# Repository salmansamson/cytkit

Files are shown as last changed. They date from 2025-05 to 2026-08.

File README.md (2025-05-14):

# Cytkit
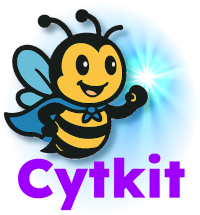
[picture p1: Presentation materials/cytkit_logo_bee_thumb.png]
Cytkit bee mascot


__Your open-source spectral cytometry sidekick__ 

## Introduction
This project was started by Samson Rogers to bring a low-cost open-source cytometer design to the cytometry community. Thanks also to Oliver Burton for contributing to the specification and Stuart Vant for starting the electronics development. The inspiration came from the Open Cytometry Hardware workshop by David Novo at CYTO 2024 in Edinburgh, and also from the OpenFlexure Microscope project by Richard Bowman and others. Thanks to many friends and colleagues for friendly advice!

Aim: to build a highly useful and accessible cytometry analyser:
- Useful for technology developers 
- Useful for laboratory hackers
- Useful for resource-limited labs
- Useful for teaching flow cytometry
- Useful for all cell biologists

Through this project, I hope to: 
- Help build the open source cytometry hardware community
- Release a simple design that is highly accessible for others to modify and build on
- Share knowledge for building cytometers and new cytometry technology

The design is currently labelled v0.3 and contains all mechanical parts, an optical model, and a bill of materials. Initial testing of the released system is underway in conjunction with commercial photodetectors, external data acquisition hardware and offline analysis, and shows that the system is capable of resolving 8 peak rainbow beads. 

To complete the design, the following additions are planned:
- PCBs for forward scatter, side scatter and fluorescence, data acquisition and fluidics control
- embedded software for peak detection
- host PC software for data acquisition, simple analysis, control of the instrument, and export of cytometry data

The bill of materials including all current parts as well as an estimation of the planned electronics currently comes to about $3k. 

Please [get in touch with me](https://www.linkedin.com/in/salmanrogers/) if you are:
- interested in contributing
- interested in buying a kit
- interested in requesting our expertise
- interested in anything else!

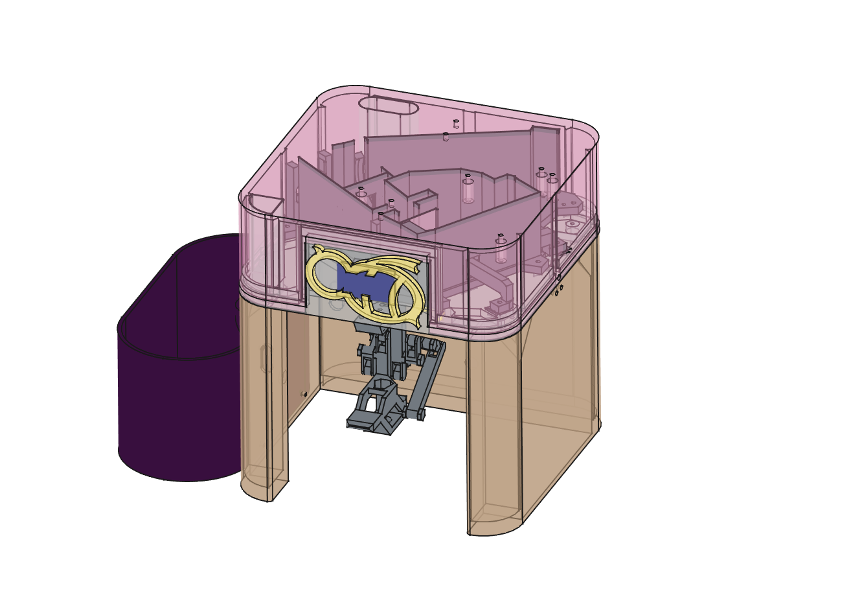
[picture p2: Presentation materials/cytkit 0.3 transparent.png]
Cytkit CAD render


## License
This project is released under the CERN Open Hardware Licence Version 2 - Strongly Reciprocal [CERN-OHL-S](https://opensource.org/license/cern-ohl-s). 

That means you can study and modify this design. You may also manufacture and distribute products based on it if you release derivative designs under the same open source license. 

There is no warranty. All liabilities are disclaimed. You accept the design "as is." 

## Specification
Cytkit is intended to be one's personal cytometry _sidekick_:
- Conventional format, but small
- Easy to adjust, align and maintain... no need for a service contract
- Separate sheath and waste bottles
- Volumetric sample pump for absolute concentration measurement of cell populations
- Conventional single SIP-tube sample loader 
- User interface on PC connected by USB
- Can be powered by USB power pack
- Mechanical parts all 3D-printed

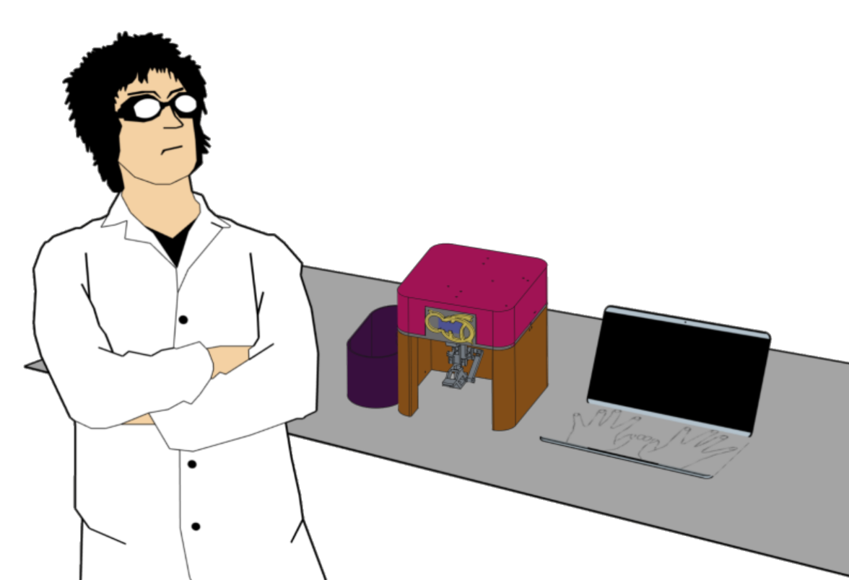
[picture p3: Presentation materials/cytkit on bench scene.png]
Cytkit bench scene with scientist


## Cytometry
The cytometry is based on a single laser plus an spectral array of solid-state detectors.

__Why?__

- Skilled cytometrists can currently measure ~10 fluorophores on a 488 nm laser alone
- Take advantage of low-cost reagents for the 488 nm laser
- Take advantage of available low-cost parts: SiPMs plus dispersion element rather than many expensive filters
- Such a design can be mechanically simple, allowing fully 3D printed mechanics, simple assembly, adjustment and alignment

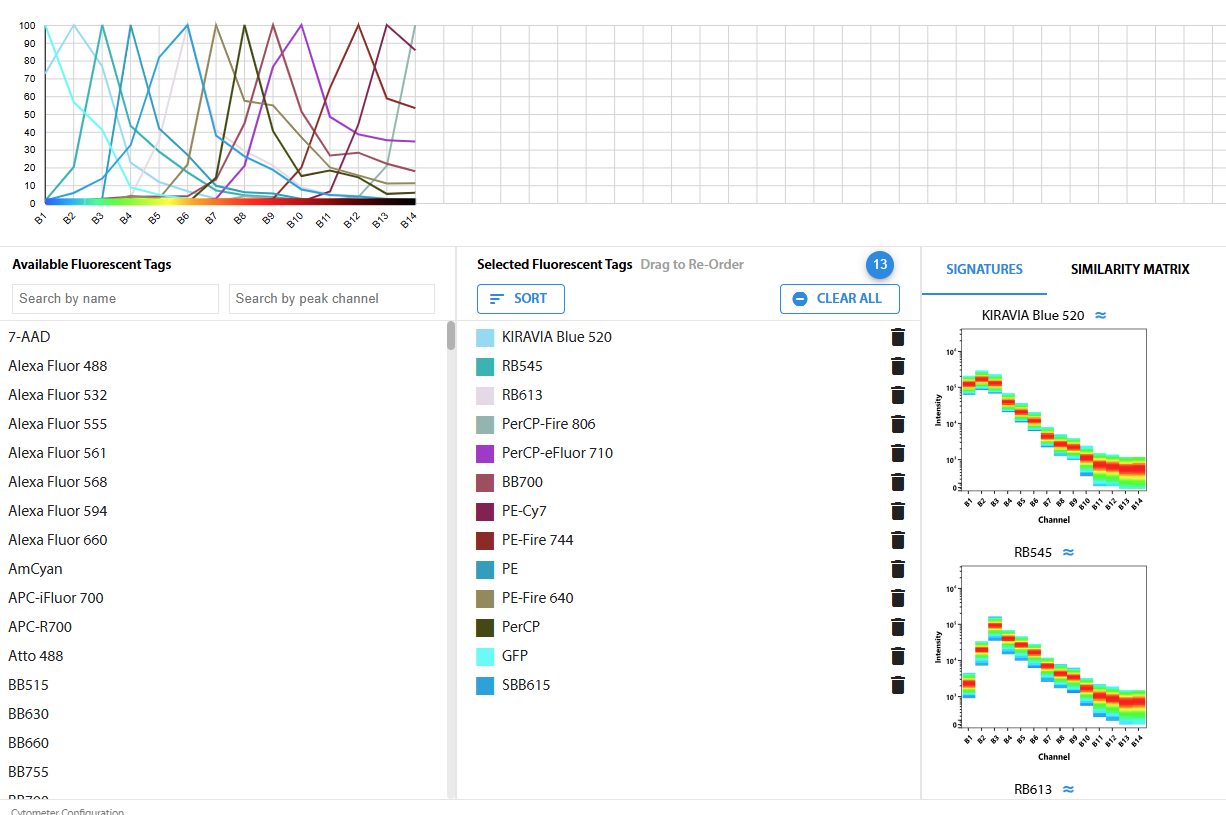
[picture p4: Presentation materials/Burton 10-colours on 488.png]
Cytkit cytometry spec


## Source files
The full mechanical design has been built with FreeCAD and is provided in [CAD and optical model/Cytkit model 0.32.FCStd](/CAD%20and%20optical%20model/Cytkit%20model%200.32.FCStd)

The optical model has been built in the FreeCAD Optical Design Workbench and is provided in [Cytkit model 0.31 12may25 optics only.FCStd](/CAD%20and%20optical%20model/Cytkit%20model%200.31%2012may25%20optics%20only.FCStd)

STL files for 3D printing (FDM) are provided in [STL files for printing](/STL%20files%20for%20printing).

The Bill of Materials including suppliers of parts is provided in [Cytkit Bill of Materials v0.3.ods](/Cytkit%20Bill%20of%20Materials%20v0.3.ods).

## To do
- Present the project at CYTO 2025 in Denver
- Write complete documentation for 3D printing, assembly, alignment and maintenance
- Provide electronics PCBs and connectors
- Provide software (embedded and host PC)
- Provide kits on demand
- Build a business to make this project rewarding for collaborators

## Safety
**Note that lasers, such as the one listed in the Bill of Materials are hazardous to the eyes. Direct exposure could cause permanent eye damage. Please do not build this design without adequate laser safety training.**

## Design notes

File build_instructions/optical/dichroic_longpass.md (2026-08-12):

---
PartData:
    Specs:
        Edge: between 490 and 500 nm
        Optical density at 488 nm: at least 4; preferably > 6
        Transmission at 500 nm: preferably > 90% 
        Diameter: 25 mm (holders also available for 34 mm circular and 25.5x36 mm rectangular)
    Suppliers:
        Semrock:
            PartNo: BLP01-488R-25
            Link: 'https://www.idex-hs.com/store/product-detail/blp01_488r_25'
        Edmund Optics:
            PartNo: '#62-983'
            Link: 'https://www.edmundoptics.com/p/500nm-25mm-dia-high-performance-longpass-filter/17600/'

---
# Dichroic longpass filter at 0 degrees

This filter is the most important barrier to stop the laser light getting into the fluorescence detectors, while being as transparent as possible to the fluorescence emissions as close to the laser line as possible. There is a significant price difference between the best dichroic longpass filters and the mediocre ones. To resolve fluorophores such as GFP, BB515 and FITC whose emissions are close to the laser line, buy a filter that is substantially transparent at wavelengths > 500 nm. To avoid loss of sensitivity, optical density should be up to 6 at 488 nm. 

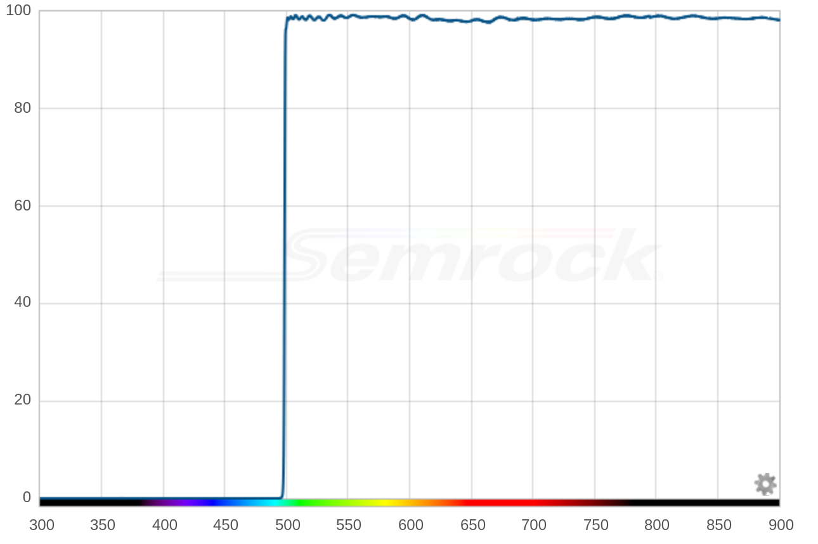
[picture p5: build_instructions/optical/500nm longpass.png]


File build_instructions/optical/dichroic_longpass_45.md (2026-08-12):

---
PartData:
    Specs:
        Edge: between 490 and 500 nm
        Dimensions: 25x36 mm rectangular, thickness 1 mm
        Angle: 45 degrees
    Suppliers:
        Semrock:
            PartNo: Di02-R488-25x36
            Link: 'https://www.idex-hs.com/store/product-detail/di02_r488_25x36'
        Edmund Optics:
            PartNo: '#69-899'
            Link: 'https://www.edmundoptics.com/p/500nm-252-x-356mm-dichroic-longpass-filter/24165/'

---
# Dichroic longpass filter at 45 degrees (Beamsplitter)

This filter splits off the majority of the laser light at 488 nm towards the SSC detector. The filter should be substantially transparent above 500 nm to avoid cutting off blue/green-emitting fluorophores such as GFP, FITC and BB515.

500nm, 25.2 x 35.6mm, Dichroic Longpass Filter  (45 Degrees)



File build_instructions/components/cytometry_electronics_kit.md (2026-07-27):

# Astute Devices Cytometry Electronics Kit CYKIT-E-1

#### For Cytkit 2S-14F, coming soon!

This kit provides all the electronics you need for a Cytkit 2S-14F:

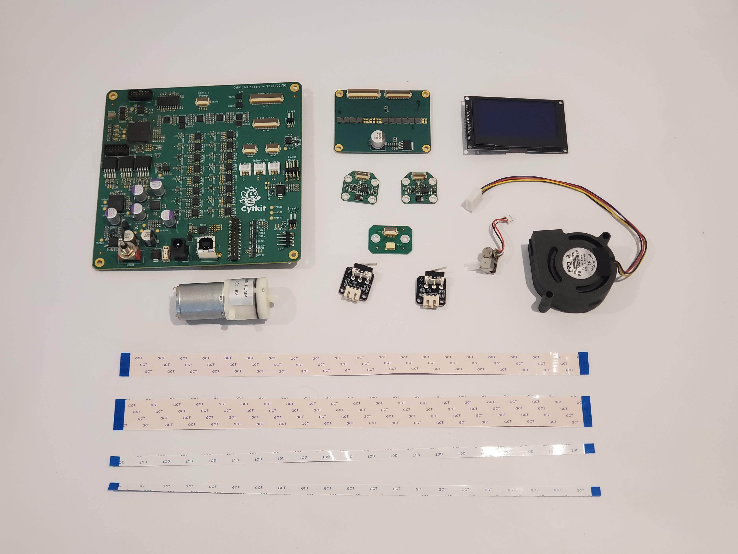
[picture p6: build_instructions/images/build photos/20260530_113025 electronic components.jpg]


1. [Cytometer control board](../electronic/cytometer_control_board.md){qty:1, cat:electronics2s14f}
1. [Photodiode board](../electronic/photodiode_board.md){qty:2, cat:electronics2s14f} x2
1. [SiPM array board](../electronic/sipm_array_board.md){qty:1, cat:electronics2s14f}
1. [Pump connector board](../electronic/pump_connector_board.md){qty:1, cat:electronics2s14f}
1. [Interlock switches](../electronic/interlock_switches.md){qty:2, cat:electronics2s14f} x2
1. [OLED display](../electronic/oled_display.md){qty:1, cat:electronics2s14f}
1. [Blower fan](../electronic/blower_fan.md){qty:1, cat:electronics2s14f}
1. [USB camera module](../electronic/camera.md){qty:1, cat:electronics1s1f}
1. [Vacuum pump for sheath](../fluidic/sheath_pump.md){qty:1, cat:fluidics}
1. [Peristaltic pump for sample](../fluidic/sample_pump.md){qty:1, cat:fluidics}
1. [Ribbon connector set](../electronic/ribbon_connectors.md){qty:1, cat:electronics2s14f}
1. [36V DC power supply](../electronic/36v_dc_power_supply.md){qty:1, cat:electronics2s14f}
1. [USB A to USB B cable](../electronic/usb_a_to_b_cable.md){qty:1, cat:electronics2s14f}

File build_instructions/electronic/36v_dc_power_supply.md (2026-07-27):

# 36V DC Power Supply

#### For the Cytkit 2S-14F configuration

Power supply for the Main Board and all connected electronics.

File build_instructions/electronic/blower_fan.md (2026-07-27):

# Blower fan

#### For the Cytkit 2S-14F configuration

A 5025 blower fan with PWM speed control and speed sensor, for thermal management of the Cytkit instrument, controlled by the Main Board.

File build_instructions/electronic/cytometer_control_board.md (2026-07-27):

# Cytometer Main Board

#### For the Cytkit 2S-14F configuration, coming soon!

Main Board for building a cytometer comprising:

- 16 channels voltage input analogue-to-digital converters (ADC)
- 16 channels reference voltage output for detectors digitally controlled (DAC)
- 16 channels bias voltage output for detectors digitally controlled (DAC)
- DC motor controller for sheath pump (to control voltage-based pumps for positive pressure or vacuum)
- Stepper motor controller for sample pump (to control stepper-based peristaltic or syringe pump)
- 5V stabile voltage power supply for laser
- Fan controller for thermal management of instrument
- Laser power supply
- FPGA with triggering firmware for real time digital signal processing 
- OLED display controller (SPI)
- USB communication chip for input / output to host PC
- USB hub for connecting on-board camera
- 2 x interlock connections for switching off laser if enclosure is opened
- 2 x PD Board connections
- 1 x SiPM Board biases and references connection
- 1 x SiPM Board signal connection
- 1 x Laser power connection
- 1 x Stepper motor connection
- 1 x DC motor connection
- 1 x Fan connection
- 2 x USB connections

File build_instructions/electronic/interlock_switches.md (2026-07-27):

# Interlock switches

#### For the Cytkit 2S-14F configuration

Interlock switches: two are connected to the Main Board. When configured correctly, if either interlock switch is opened (by removing the instrument cover), the laser is switched off.

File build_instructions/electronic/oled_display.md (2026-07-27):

# OLED Display

#### For the Cytkit 2S-14F configuration

Front panel display connects to the Main Board to display instrument status.

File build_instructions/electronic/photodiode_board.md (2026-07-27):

# Photodiode Board

#### For the Cytkit 2S-14F configuration, coming soon!

Detector board containing:

- one silicon photodiode (PD), suitable for detecting forward or side scatter, either as positive (dark field, true small/wide angle light scatter) or negative (occultation, light loss, brightfield)
- analog electronics for the PD chip, comprising reference voltage connection, transimpedance amplifier and voltage output
- ribbon connector for power, reference and voltage output to the Main Board

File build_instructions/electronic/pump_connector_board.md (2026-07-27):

# Pump connector board

#### For the Cytkit 2S-14F configuration

A breakout board to connect the sample peristaltic pump (JST SH 1.0mm 4-pin connector) to the Main Board (ribbon cable).

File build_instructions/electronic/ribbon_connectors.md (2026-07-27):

# Ribbon Connectors

#### For the Cytkit 2S-14F configuration

Set of ribbon connectors to connect the Main Board to 1x SiPM board, 2x PD boards, 1x pump connector board.

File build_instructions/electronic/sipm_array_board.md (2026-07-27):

# SiPM Array Board

#### For the Cytkit 2S-14F configuration, coming soon!

Detector board containing:

- one row of 14 silicon photomultipliers (SiPM) suitable for detecting a full spectrum of fluorescence emission 
- analog electronics for each individual SiPM chip, comprising bias voltage connection, reference voltage
connection, transimpedance amplifier and voltage output
- ribbon connectors for bias voltage and reference voltage controls and voltage outputs to the Main Board

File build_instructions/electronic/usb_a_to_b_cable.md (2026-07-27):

# USB A to USB B Cable

#### For the Cytkit 2S-14F configuration, coming soon!

To connect the Main Board (USB B socket) to the host PC (USB A socket).

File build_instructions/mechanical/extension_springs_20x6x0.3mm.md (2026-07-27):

---
PartData:
    Specs:
        Length: 20 mm
        Diameter: 6 mm
        Wire diameter: 0.3 mm
        Material: stainless steel
    Suppliers:
        Aliexpress:
            PartNo: N/A 
            Link: 'https://www.aliexpress.com/item/1005007596268334.html'
---
# Extension spring 20x6x0.3mm

Compression springs for maintaining the two stable positions of the sample loader. 1 required.



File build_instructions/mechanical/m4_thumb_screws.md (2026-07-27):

---
PartData:
    Specs:
        Length: 10 mm
        Thread: M4
    Suppliers:
        Aliexpress:
            PartNo: N/A 
            Link: 'https://www.aliexpress.com/item/1005010135215669.html'
---
# Thumb screws

For fastening the cover. 3 required



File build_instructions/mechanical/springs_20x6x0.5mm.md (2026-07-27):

---
PartData:
    Specs:
        Length: 20 mm
        Diameter: 6 mm
        Wire diameter: 0.5 mm
        Material: stainless steel
    Suppliers:
        Aliexpress:
            PartNo: N/A 
            Link: 'https://www.aliexpress.com/item/1005002531385040.html'
---
# Springs (compression) 20x6x0.5mm

Compression springs for adjustment of the flexural degrees of freedom. 7 required.



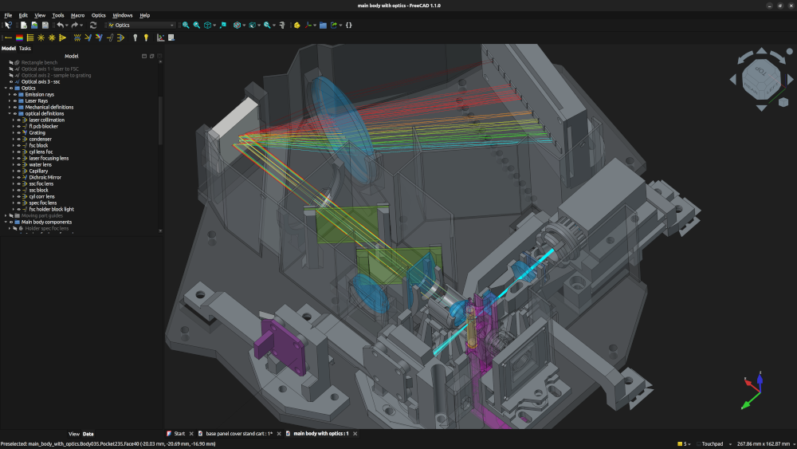
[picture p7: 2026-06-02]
build_instructions/images/cytkit optical model in freecad small.png

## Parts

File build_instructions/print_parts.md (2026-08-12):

# Print the mechanical parts

Almost all the mechanical parts of the Cytkit are 3D printed, which you can do yourself from the STL files provided in the repo. Most parts require a consumer-grade FDM 3D printer with a 220x220mm print bed. A few parts however require a resin printer, for fine detail and fluidic sealing. 

>i A couple of days of 3D printing is required to build a Cytkit, and both an FDM and a resin printer. We intend to supply full kits shortly to make it easier to get started with Cytkit.

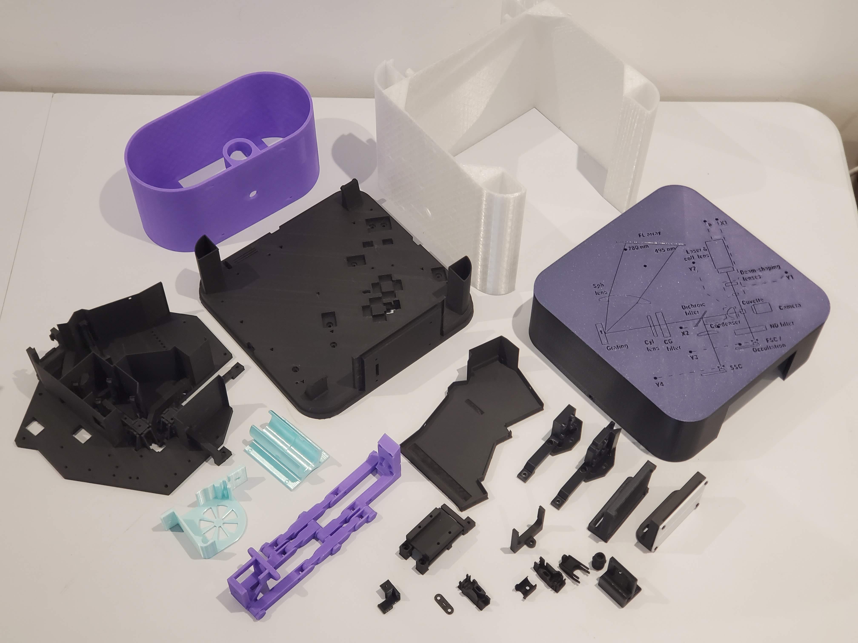
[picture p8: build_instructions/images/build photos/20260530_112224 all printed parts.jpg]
All printed parts


# FDM parts

## Matt black PLA parts

The following parts should be printed in matt black PLA. Their blackness is important for absorption of stray light. Their rigidity is important to keep a fixed alignment. Any PLA variant that is rigid and very matt will do, e.g. Ultra PLA.

1. [Main body](printed/main_body.md){qty:1, cat:printed}
1. [Base](printed/base.md){qty:1, cat:printed}
1. [Laser holder](printed/laser_holder.md){qty:1, cat:printed}
1. [Holder SiPM board](printed/holder_sipm_board.md){qty:1, cat:printed}

For the Cytkit 1S-1F configuration:

1. [Fluorescence compartment cap for PMT](printed/fluorescence_compartment_cap_pmt.md){qty:1, cat:printed1S1F}
1. [Amplified PD holder](printed/Amplified_PD_holder.md){qty:1, cat:printed1S1F}
1. [PMT mount base](printed/PMT_mount_base.md){qty:1, cat:printed1S1F}
1. [PMT mount](printed/PMT_mount.md){qty:1, cat:printed1S1F}
1. [Cover (with cable holes)](printed/Cover_with_cable_holes.md){qty:1, cat:printed1S1F}

For the Cytkit 2S-14F configuration:

1. [Fluorescence compartment cap](printed/fluorecence_compartment_cap.md){qty:1, cat:printed2S14F}
1. [PD board holder (h-adjust)](printed/pd_holder_h.md){qty:1, cat:printed2S14F}
1. [FSC v-slit 0.4mm](printed/fsc_v_slit.md){qty:1, cat:printed2S14F}
1. [PD board holder (v-adjust h-slit)](printed/pd_board_holder_v.md){qty:1, cat:printed2S14F}
1. [ND filter holder for FSC](printed/nd_filter_holder.md){qty:1, cat:printed2S14F}
1. [Holder SiPM board](printed/holder_sipm_board.md){qty:1, cat:printed} (print an additional one to the one listed above)
1. [Cover (with optics diagram)](printed/cover_with_optics_diagram.md){qty:1, cat:printed1S1F}
1. [Cable stay bar](printed/cable_stay_bar.md){qty:1, cat:printed1S1F}

>i Note that the Cover (with optics diagram) can be printed with a couple of external layers in a different colour, for decoration and for better contrast in visualising the optics diagram.

## Black PLA+ parts

The following parts should also be rigid and black, but require a bit more flexibility to hold optics firmly or allow flexural degrees of freedom. Therefore PLA+ is recommended.

1. [Focusing lens holders](printed/foc_lens_holder.md){qty:1, cat:printed}
1. [Condensing lens holder](printed/condensing_lens_holder.md){qty:1, cat:printed}
1. [Correction cylindrical lens holder](printed/correction_cyl_lens_holder.md){qty:1, cat:printed}
1. [Camera mount v-adjust](printed/camera_mount_v_adjust.md){qty:1, cat:printed}
1. [Circular filter holder (26mm diameter)](printed/coloured_glass_filter_holder.md){qty:2, cat:printed}
1. [Grating holder](printed/grating_holder.md){qty:1, cat:printed}
1. [Spectrum focusing lens holder](printed/spectrum_focus_lens_holder.md){qty:1, cat:printed}
1. [LED holder for fluorescence and SSC testing](printed/led_holder_fl_ssc_test.md){qty:1, cat:printed}
1. [SSC focusing lens holder](printed/ssc_focus_lens_holder.md){qty:1, cat:printed}

Since a variety of filter sizes are available from optics suppliers as stock items, we also provide a set of alternative size holders:

1. [Circular filter holder (34mm diameter)](printed/circular_filter_holder_34mm_diameter.md){qty:1, cat:printed}
1. [Circular filter holder (25mm diameter)](printed/circular_filter_holder_25mm_diameter.md){qty:1, cat:printed}
1. [Circular filter holder (15mm diameter)](printed/circular_filter_holder_15mm_diameter.md){qty:1, cat:printed}
1. [Rectangular filter holder (25.5x26mm)](printed/rectangular_filter_holder.md){qty:1, cat:printed}

## White PLA parts

The following part must be printed in white as it is a tool for seeing the spectrum in coarse alignment:

1. [FL screen](printed/fl_screen.md){qty:1, cat:printed}

## Any-colour-you-like parts (PLA+ recommended)

The following parts do not interfere with the optics, and therefore can be printed in any colour you like. PLA+ is recommended for toughness, ridigity and accuracy.

1. [Sample loader](printed/sample_loader.md){qty:1, cat:printed}
1. [Sample loader range limiter](printed/sample_loader_range_limiter.md){qty:1, cat:printed}
1. [Sample pump holder](printed/sample_pump.md){qty:1, cat:printed}

For the Cytkit 1S-1F configuration:

1. [Front panel logo](printed/front_panel_logo.md){qty:1, cat:printed1S1F}

## Tough parts (PETG recommended)

The following parts can be printed in any colour. PETG is recommended for toughness and durability.

1. [Stand](printed/stand.md){qty:1, cat:printed}
1. [Fluidics cart](printed/fluidics_cart.md){qty:1, cat:printed}
1. [Rear panel cover](printed/rear_panel_cover.md){qty:1, cat:printed}

## Flexible parts (TPU recommended)

The following parts can be printed in any colour. TPU is recommended to absorb noise and vibration.

1. [Sheath pump holder](printed/sheath_pump_holder.md){qty:1, cat:printed}
1. [Fan holder](printed/fan_holder.md){qty:1, cat:printed}

# Resin parts

The following parts should all be printed using a resin printer (e.g. an LCD printer) in black resin (e.g. ABS-like black resin). The resin print has much higher resolution than FDM and allows proper sealing of fluidic parts as well as accurate printing of fine threads.

1. [Sheath chamber](printed/sheath_chamber.md){qty:1, cat:printed_resin}
1. [Laser collimating lens lock nut](printed/lock_nut.md){qty:1, cat:printed_resin}
1. [Laser collimating lens lock nut adjustment tool (short)](printed/lock_nut_tool_short.md){qty:1, cat:printed_resin}
1. [Laser collimating lens lock nut adjustment tool (long)](printed/lock_nut_tool_long.md){qty:1, cat:printed_resin}
1. [Camera tube lens](printed/camera_tube_lens.md){qty:1, cat:printed_resin}

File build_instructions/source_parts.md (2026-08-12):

# Source the optical, electronic, fluidic and mechanical components

Apart from the 3D printed parts, Cytkit requires a set of specialised components: optical, electronic and fluidic, as well as a few non-printed mechanical components. These are listed below along with recommended sources.

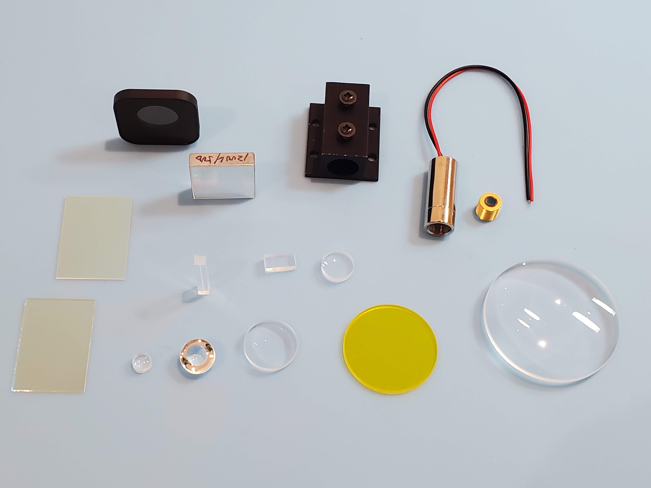
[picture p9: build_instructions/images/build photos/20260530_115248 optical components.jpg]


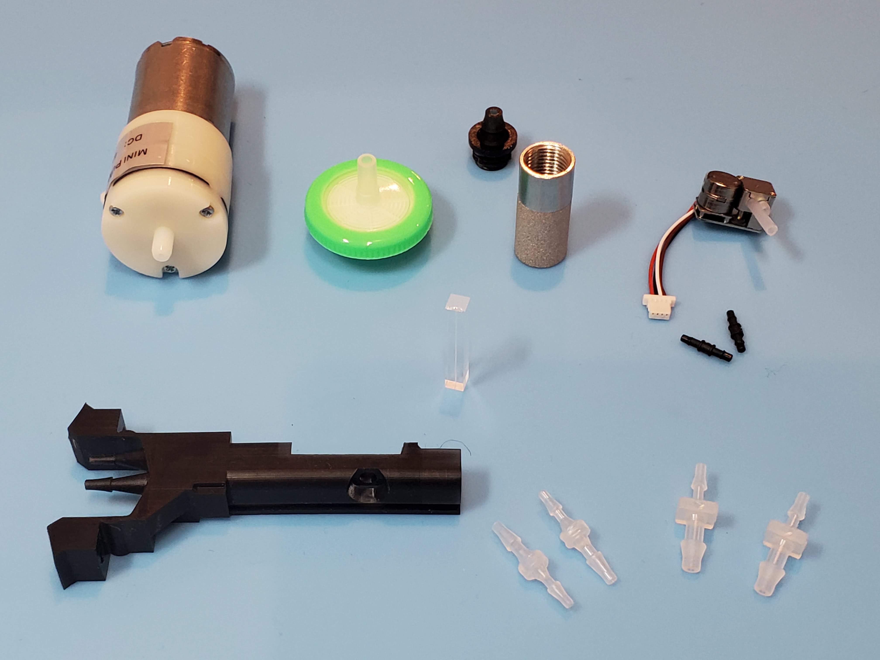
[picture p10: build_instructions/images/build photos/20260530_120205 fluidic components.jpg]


>i We intend to supply full kits shortly, with all recommended components, to make it easier to get started with Cytkit.

## Source the safety equipment

1. [Laser safety glasses](safety/laser_safety_glasses.md){qty:1, cat:safety}

## Source the optical components

1. [Laser focus lens spherical](optical/laser_focus_lens_spherical.md){qty:1, cat:optics}
1. [Laser focus lens cylindrical](optical/laser_focus_lens_cylindrical.md){qty:1, cat:optics}
1. [Blazed reflection grating](optical/blazed_reflection_grating.md){qty:1, cat:optics}
1. [Neutral density filter](optical/nd_filter.md){qty:1, cat:optics}
1. [Dichroic longpass filter at 45 degrees (beamsplitter)](optical/dichroic_longpass_45.md){qty:1, cat:optics}
1. [Dichroic longpass filter at 0 degrees](optical/dichroic_longpass.md){qty:1, cat:optics}
1. [Coloured glass longpass filter](optical/coloured_glass_longpass.md){qty:1, cat:optics}
1. [Condensing lens](optical/condensing_lens.md){qty:1, cat:optics}
1. [Spectrum focusing lens](optical/spectrum_focusing_lens.md){qty:1, cat:optics}
1. [SSC focusing lens](optical/ssc_focusing_lens.md){qty:1, cat:optics}
1. [F7D8 aspherical lens](optical/F7D8_aspherical_lens.md){qty:2, cat:optics}
1. [488 nm laser module](optical/laser_module.md){qty:1, cat:optics}
1. [Laser collimating lens](optical/laser_collimating_lens.md){qty:1, cat:optics}
1. [Laser heatsink](optical/laser_heatsink.md){qty:1, cat:optics}
1. [Band pass dichroic filter](optical/band_pass_dichroic.md){qty:1, cat:optics}
1. [Cylindrical correction lens](optical/cylindrical_correction_lens.md){qty:1, cat:optics}

## Source the fluidic components

1. [Vacuum pump for sheath](fluidic/sheath_pump.md){qty:1, cat:fluidics}
1. [Peristaltic pump for sample](fluidic/sample_pump.md){qty:1, cat:fluidics}
1. [Bottom-of-bottle filter](fluidic/bottom_of_bottle_filter.md){qty:1, cat:fluidics}
1. [Silicone tubing 1 mm ID](fluidic/silicone_tubing_1mm.md){qty:1, cat:fluidics}
1. [Silicone tubing 1.6 mm ID](fluidic/silicone_tubing_1.6mm.md){qty:1, cat:fluidics}
1. [Silicone tubing 4 mm ID](fluidic/silicone_tubing_4mm.md){qty:1, cat:fluidics}
1. [Tube barb union 1.6x2.4](fluidic/tube_barb_union1.6x2.4.md){qty:2, cat:fluidics}
1. [Tube barb union 1.6x3.2](fluidic/tube_barb_union1.6x3.2.md){qty:2, cat:fluidics}
1. [Tube barb union 2.4x6.4](fluidic/tube_barb_union2.4x6.4.md){qty:2, cat:fluidics}
1. [Quartz cuvette or thick-walled capillary](fluidic/cuvette.md){qty:1, cat:fluidics}
1. [Pressure-resistant bottle](fluidic/pressure_resistant_bottle.md){qty:1, cat:fluidics}
1. [Peek tubing 1.6mm OD 0.25mm ID](fluidic/peek_tubing.md){qty:1, cat:fluidics}

## Source the electronic components

According to the configuration you are building:

### For the Cytkit 1S-1F configuration:

1. [Amplified photodiode (Thorlabs PDA10)](components/thorlabs_pda10.md){qty:1, cat:electronics1s1f}
1. [Photomultiplier tube module (Hamamatsu H10732)](components/hamamatsu_H10732.md){qty:1, cat:electronics1s1f}
1. [USB oscilloscope (Picoscope 5000 series)](components/picoscope.md){qty:1, cat:electronics1s1f}
1. [Vacuum pump controller board](electronic/vacuum_pump_controller.md){qty:1, cat:electronics1s1f}
1. [Stepper motor controller board](electronic/stepper_controller.md){qty:1, cat:electronics1s1f}
1. [BNC (Male) to BNC (Male) cable, 1 m](electronic/bnc_cable.md){qty:1, cat:electronics1s1f}
1. [SMA (Female) to BNC (Male) adapter](electronic/sma_bnc_adapter.md){qty:1, cat:electronics1s1f}
1. [Linear Power Supply](electronic/linear_power_supply.md){qty:1, cat:electronics1s1f}
1. [Laboratory Power Supply](electronic/laboratory_power_supply.md){qty:1, cat:electronics1s1f}
1. [USB camera module](electronic/camera.md){qty:1, cat:electronics1s1f}

### For the Cytkit 2S-14F configuration:

>i All electronic components are available in the Astute Devices Cytometry Electronics Set CYKIT-E-1, or in the Cytkit Full Kit CYKIT-K-1, anticipated to launch Q4 2026. Further details coming soon!

1. [Cytometer control board](electronic/cytometer_control_board.md){qty:1, cat:electronics2s14f}
1. [Photodiode board](electronic/photodiode_board.md){qty:2, cat:electronics2s14f} x2
1. [SiPM array board](electronic/sipm_array_board.md){qty:1, cat:electronics2s14f}
1. [Pump connector board](electronic/pump_connector_board.md){qty:1, cat:electronics2s14f}
1. [Interlock switches](electronic/interlock_switches.md){qty:2, cat:electronics2s14f} x2
1. [OLED display](electronic/oled_display.md){qty:1, cat:electronics2s14f}
1. [Blower fan](electronic/blower_fan.md){qty:1, cat:electronics2s14f}
1. [USB camera module](electronic/camera.md){qty:1, cat:electronics1s1f}
1. [Ribbon connector set](electronic/ribbon_connectors.md){qty:1, cat:electronics2s14f}
1. [36V DC power supply](electronic/36v_dc_power_supply.md){qty:1, cat:electronics2s14f}
1. [USB A to USB B cable](electronic/usb_a_to_b_cable.md){qty:1, cat:electronics2s14f}

## Source the mechanical components

1. [M3 self-tapping hex socket cap screws 25 mm](mechanical/screws.yaml#self_tapping_m3x25_hex_socket){qty:1, cat:mechanics}
1. [M3 self-tapping posi head screws 6 mm](mechanical/screws.yaml#self_tapping_m3x6_posi){qty:1, cat:mechanics}
1. [M3 self-tapping posi head screws 8 mm](mechanical/screws.yaml#self_tapping_m3x8_posi){qty:1, cat:mechanics}
1. [M3 self-tapping posi head screws 10 mm](mechanical/screws.yaml#self_tapping_m3x10_posi){qty:1, cat:mechanics}
1. [M3 self-tapping posi head screws 12 mm](mechanical/screws.yaml#self_tapping_m3x12_posi){qty:1, cat:mechanics}
1. [M3 self-tapping posi head screws 16 mm](mechanical/screws.yaml#self_tapping_m3x16_posi){cat:mechanics}
1. [M3 washers](mechanical/screws.yaml#m3_washers){qty:1, cat:mechanics}
1. [Stainless steel compression springs, 0.5 mm wire, 20 mm length, 6 mm diameter](mechanical/springs_20x6x0.5mm.md){qty:1, cat:mechanics}
1. [Stainless steel extension springs, 0.3 mm wire, 20 mm length, 6 mm diameter](mechanical/extension_springs_20x6x0.3mm.md){qty:1, cat:mechanics}
1. [M4 thumb screws 10mm](mechanical/m4_thumb_screws.md){qty:3, cat:mechanics}

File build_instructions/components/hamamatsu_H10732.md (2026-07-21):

---
PartData:
    Specs:
        Item: PMT module
        Power supply: +5, 0, -5 V
        Bias voltage control: 0 -- 1 V
        Signal output: SMA connector
    Suppliers:
        Hamamatsu:
            PartNo: H10723-20
            Link: 'https://www.hamamatsu.com/us/en/product/optical-sensors/pmt/pmt-module/voltage-output-type/H10723-20.html'
---

# Photomultiplier tube module 

>i (For Cytkit 1S-1F only. Not required for Cytkit 2S-14F.)

The recommended PMT module is the Hamamatsu H10723-series which is a PMT packaged with an internal high voltage power supply, bias voltage control, and transimpedance amplifier to give a voltage output. 

The peak signal to noise ratio occurs at control voltage ~ 500 mV. 

The module can be set up with low noise laboratory power supplies to supply the +5/0/-5 V and control voltage. Alternatively, the latter can be set up on a potentiometer connected to a 1 V reference supplied by the module itself. See datasheet for recommended wiring.



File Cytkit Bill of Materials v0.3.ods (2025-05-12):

Parts in v0.3
Category | Component | Supplier | Model | Mechanical info | Source
Optics | Laser diode module | eBay or elsewhere | 488nm 30mW laser diode in 12mm x 50mm cylindrical housing | Cylinder OD 12 mm, length 50 mm | Various
Optics | Laser collimating lens | Thorlabs | C775TMD-A - f = 4.0 mm, NA = 0.60, WD = 1.5 mm, Mounted Aspheric Lens, ARC: 350 - 700 nm | M9 | https://www.thorlabs.com/thorproduct.cfm?partnumber=C775TMD-A
Optics | Laser focusing lens | Thorlabs | Ø1/2" UV Fused Silica Plano-Convex Lenses, AR Coated: 400 - 1100 nm, F40mm | R18.4 mm, Tc 2.9 mm, Te1.8 mm | https://www.thorlabs.com/thorproduct.cfm?partnumber=LA4130-AB
Optics | Condensing lens | Thorlabs | ACL1512U - Aspheric Condenser Lens, Ø15 mm, f=12 mm, NA=0.61, Uncoated |  | https://www.thorlabs.com/thorproduct.cfm?partnumber=ACL1512U
Optics | Cylindrical lens | Thorlabs | LJ1277L2-B - f = 250.00 mm, H = 20.00 mm, L = 40.0 mm, N-BK7 Plano-Convex Cylindrical Lens, Antireflection Coating: 650-1050 nm |  | https://www.thorlabs.com/thorproduct.cfm?partnumber=LJ1277L2-B
Optics | Long pass coloured glass filter | Thorlabs | FGL495M - Ø25 mm GG495 Colored Glass Filter, SM1-Threaded Mount, 495 nm Longpass | 30.5mm mounted | https://www.thorlabs.com/thorproduct.cfm?partnumber=FGL495M
Optics | Long pass dichroic filter | Thorlabs | DMLP505 - Ø1" Longpass Dichroic Mirror, 505 nm Cut-On | Mounted, 1 inch | https://www.thorlabs.com/thorproduct.cfm?partnumber=DMLP505
Optics | Grating | Thorlabs | GR25-1205 - Ruled Reflective Diffraction Grating, 1200/mm, 500 nm Blaze, 25 mm x 25 mm x 6 mm | Cuboid 25 x 25 x 6 mm | https://www.thorlabs.com/thorproduct.cfm?partnumber=GR25-1205
Optics | Spectrum focusing lens | Thorlabs | LA1050-AB - N-BK7 Plano-Convex Lens, Ø2", f = 100 mm, AR Coating: 400 - 1100 nm |  | https://www.thorlabs.com/thorproduct.cfm?partnumber=LA1050-AB
Fluidics | Peristaltic pump | Motor Guys via Aliexpress | DC 5V Micro 8mm Gear Stepper Motor Metering Precision Peristaltic Pump | 8 x 9.6 x 15.7 mm. Drawing in link | https://www.aliexpress.com/item/1005007495087617.html
Fluidics | Pressure pump | Motor Star Store via AliExpress | 6V Small Mini 370 Motor Diaphragm Air Pump Vacuum Pump Negative Pressure Suction Pump DIY Breast Pump Inflator Aquarium |  | https://www.aliexpress.com/item/1005007330201717.html
Fluidics | Tubing 2mm OD 1mm ID | JIAYI Official Store via AliExpress | 5M Transparent Flexible Silicone Tubing ID 0.5 1 1.5 2 2.5 3 3.5 4 mm Food Grade Tube Pipe Temperature Resistance Nontoxic |  | https://www.aliexpress.com/item/1005003176927357.html
Fluidics | Tubing 6mm OD 4mm ID | JIAYI Official Store via AliExpress | 5M Transparent Flexible Silicone Tubing ID 0.5 1 1.5 2 2.5 3 3.5 4 mm Food Grade Tube Pipe Temperature Resistance Nontoxic |  | https://www.aliexpress.com/item/1005003176927357.html
Fluidics | Pressure-resistant bottle | Eloop-Sr Store via AliExpress | 2 pcs 1L Soda Carbonating PET Bottle multiple colors including white, black, green, grey, yell |  | https://www.aliexpress.com/item/1005006391360480.html
Fluidics | Syringe filter 0.2um | Daily deals Store via AliExpress | PES 25MM0.22um (5/10/25pcs PTFE PES MCE PVDF Nylon Industrial Syringe Filters 13-33mm 0.22-0.45m Chemistry Labware Random Color Filter Mask ) |  | https://www.aliexpress.com/item/1005004488186154.html
Fluidics | Luer female to 1.6mm barb adapter | Cole Parmer | Cole-Parmer Luer to Hose Barb Fitting, Straight Adapter, Animal-Derivative-Free Polypropylene, Cleanroom Packed, Female Luer x 1/16" ID; 10/Pk |  | https://www.coleparmer.co.uk/i/cole-parmer-luer-to-hose-barb-fitting-straight-adapter-animal-derivative-free-polypropylene-cleanroom-packed-female-luer-x-1-16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
Fluidics | Luer male to 1.6mm barb adapter | Cole Parmer | Cole-Parmer Luer to Hose Barb Fitting, Straight Adapter, Animal-Derivative-Free Polypropylene, Cleanroom Packed, Male Luer Lock x 1/16" ID; 10/Pk |  | https://www.coleparmer.co.uk/i/cole-parmer-luer-to-hose-barb-fitting-straight-adapter-animal-derivative-free-polypropylene-cleanroom-packed-male-luer-lock-x-1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
Fluidics | Glass capillary | Camlab | Disposable Micro-Pipette (Total) 2µl (Lambda) Pack of 100 |  | https://www.camlab.co.uk/disposable-micro-pipette-total-2-l-lambda-pack-of-100
Fluidics | Fret filter | IDEX via Cole Parmer | Idex Inlet Solvent Filter, Stem, SS, 10 µm, 1/16" ID Tubing; 1/EA |  | https://www.coleparmer.co.uk/i/idex-inlet-solvent-filter-stem-ss-10-m-1-16-id-tubing-1-ea/4270100
Fluidics | PEEK tubing 1.6mm OD 0.25mm ID | IDEX via Cole Parmer | Idex 1531B Chromatography Tubing, Blue PEEK, 1/16" OD x 0.010" ID x 5 ft L; 1/EA |  | https://www.coleparmer.co.uk/i/idex-1531b-chromatography-tubing-blue-peek-1-16-od-x-0-010-id-x-5-ft-l-1-ea/0200610
Mechanics | Filament – PLA+, Black, 1kg
Mechanics | Filament – PETG, Clear, 1kg
Mechanics | M3 self tapping screws 10mm countersunk | KK Fa$hion Space via AliExpress | 20/50pcs M2 M3 Small Micro Carbon Steel Cross Phillips Flat Countersunk Pan Head Self Tapping Wood Screw Machine Laptop Screws 50pcs, M3x10mm |  | https://www.aliexpress.com/item/1005004177352184.html
Mechanics | M3 self tapping screws set | NINDEJIN NINDEJIN Official Store | 450pcs/set Black Plated Round Pan Head Tapping Screws Set M2.3 M2.6 M3 Carbon Steel Comp |  | https://www.aliexpress.com/item/4001014733674.html
Mechanics | M4 bolt 8mm | Chang Da Store via AliExpress | 5pcs-10pcs M2 M2.5 M3 M4 M5 M6 Steel with black or 304 Stainless Steel Thumb Screws Small Knurled Head Manual Adjustment Screws 304 Stainless Steel, M4 5pcs, 8mm |  | https://www.aliexpress.com/item/1005004559808799.html
Mechanics | M3 self tapping screws – hex – 25mm | JUIDINTO Official Store via AliExpress | JUIDINTO 15-50pcs Black Hex Hexagon Socket Cap Head Self Tapping Screws Carbon Steel, 40pc |  | https://www.aliexpress.com/item/1005004723738740.html
Mechanics | M2.3 self tapping screws
Total | Cost GBP | Cost USD
Current parts v0.3 prices | 910 | 1201
Further parts (electronics fully assembled) estimated | 1200 | 1584
Total | 2110 | 2785

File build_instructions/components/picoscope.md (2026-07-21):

---
PartData:
    Specs:
        Item: USB digital oscilloscope
        Bandwidth: ">= 60 MHz"
        Channels: ">= 2"
        Input connectors: BNC
    Suppliers:
        Pico Technology:
            PartNo: 5442D
            Link: 'https://www.picotech.com/oscilloscope/5000/flexible-resolution-oscilloscope?kit=5442D'
---

# USB digital oscilloscope (Picoscope 5000-Series)

>i (For Cytkit 1S-1F only. Not required for Cytkit 2S-14F.)

The recommended USB digital oscilloscope is any of the Picoscope 5000-Series. The Picoscope software is used for alignment. The relevant Honeychrome driver acquires data using the Picoscope SDK.



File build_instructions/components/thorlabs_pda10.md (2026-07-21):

---
PartData:
    Specs:
        Item: Photodiode module
    Suppliers:
        Thorlabs:
            PartNo: PDA10A
            Link: 'https://www.thorlabs.com/item/PDA10A'
---
# Amplified photodiode 

>i (For Cytkit 1S-1F only. Not required for Cytkit 2S-14F.)

The recommended photodiode module is the Thorlabs PDA10 or PDA10A2, which is an amplified silicon photodiode with its own power supply and BNC output. This may be used for FSC as occultation (light loss) or small angle light scatter.



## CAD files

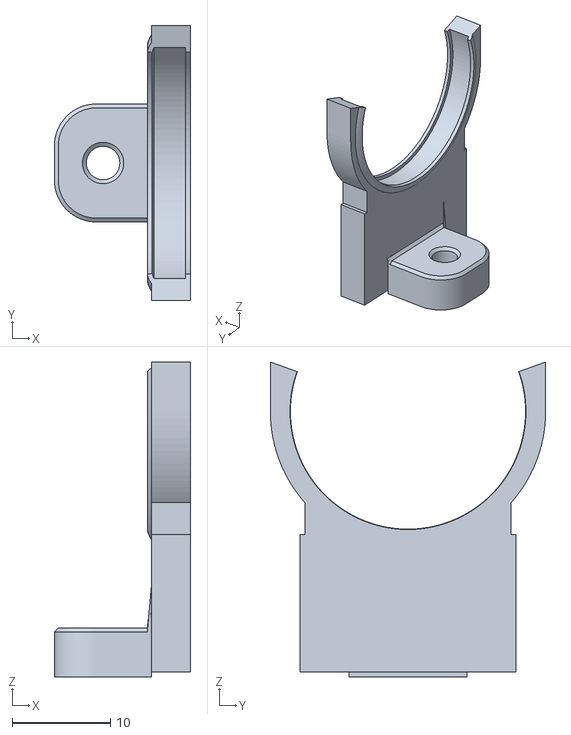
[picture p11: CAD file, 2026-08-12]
build_instructions/printed/stl/main body with optics-Filter holder D25mm.stl
13.8 x 28.0 x 32.0

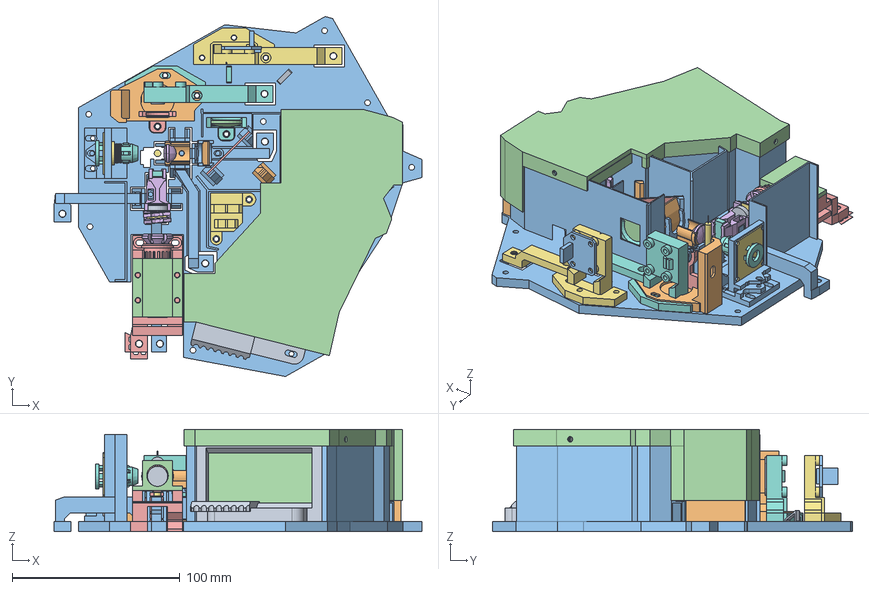
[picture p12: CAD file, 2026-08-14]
CAD and optical model/main body with optics.FCStd
219.1 x 214.4 x 61.0 mm
laser
Spectrum foc lens
Grating cube
PCB placeholder
laser collmating lens C775TMD-A - f = 4.0 mm, NA = 0.60, WD = 1.5 mm, Mounted Aspheric Lens, ARC: 350 - 700 nm
water
capillary quartz 4mm (round)
12X6mm Plano Convex Cylindrical Lens K9 Optical Glass Focal Length 27mm Center Thickness 4mm
Fused Silica 12.7mm Diameter Optical Plano Convex Lens Focal Length 50
corr cyl lens glass
SSC board
ssc foc lens f=50mm
dichroic filter 1
F8D12.7 aspherical condensing lens ACL 12708U CTN002243-E0W
bandpass
cable stay
cable stay 2
dichroic holder 2a
Main body
laser heat sink
lock nut
focusing lens holders
ssc holder
PD holder h adjust
fsc v slit 0.4mm
condensing lens holder
corr cyl lens holder
fluorescence compartment cap
Holder Laser 25mW
colimating lens adjustment tool - short
LED holder for FL+SSC testing
ssc foc lens holder
Holder FL board - extra airflow to rear
Holder grating
Holder spec foc lens
Filter holder D34mm
Filter holder D15mm
Filter holder D25mm
camera OV9726 25x30mm module
camera lens tube
mount test PMT
PDA10A holder v adjust
camera focus mount - v adjust 2

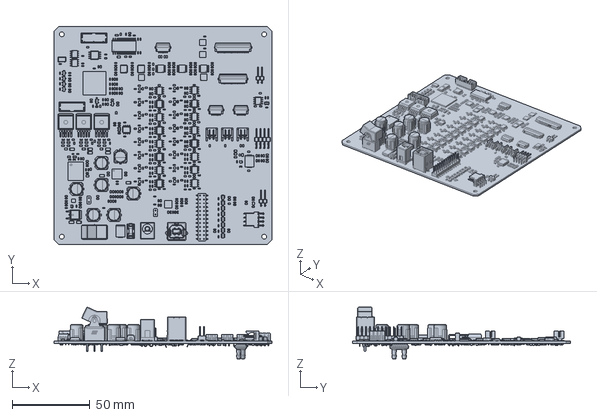
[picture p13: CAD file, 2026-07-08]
CAD and optical model/PCB exports/main pcb.FCStd
140.0 x 140.0 x 33.1 mm

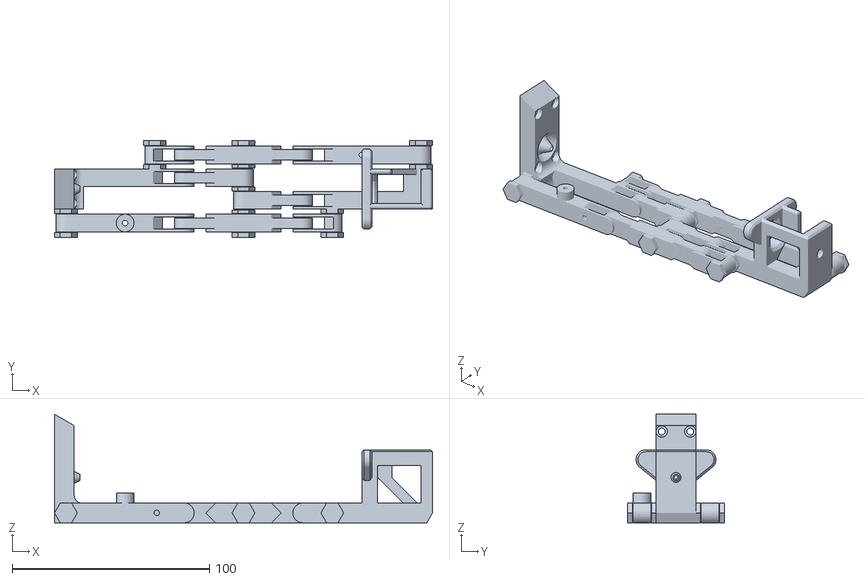
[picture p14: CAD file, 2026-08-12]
build_instructions/printed/stl/sample loader - assembly flat.stl
191.5 x 49.2 x 55.0

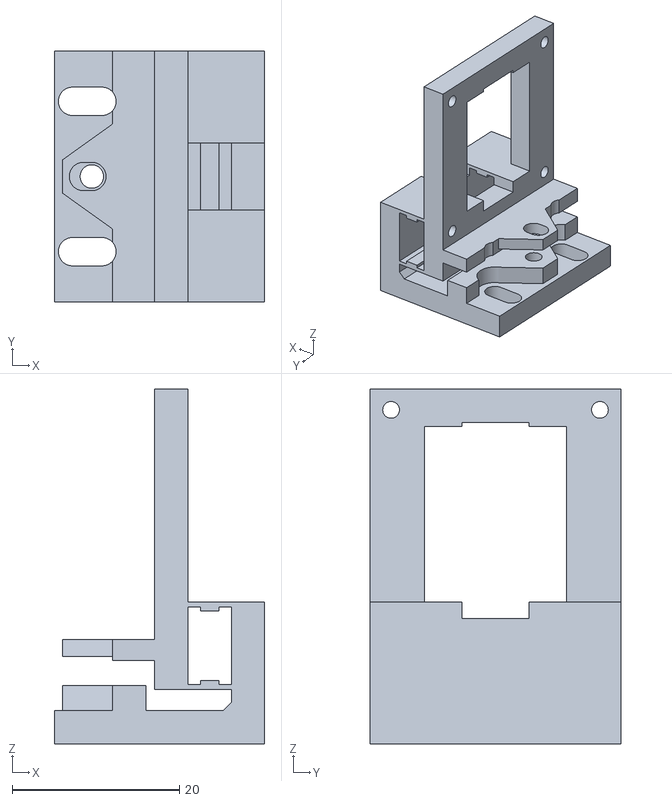
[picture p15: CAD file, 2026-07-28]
build_instructions/printed/stl/main body with optics-camera focus mount - v adjust.stl
25.2 x 30.0 x 42.5

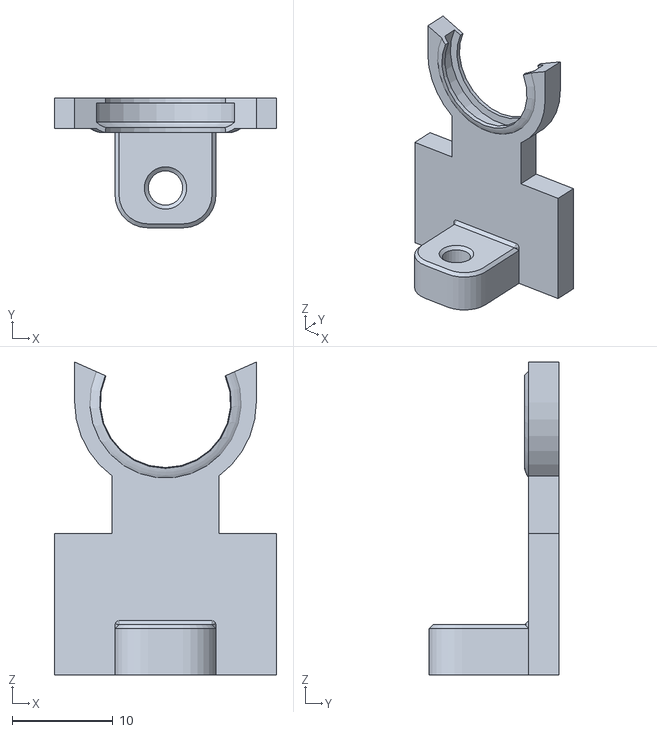
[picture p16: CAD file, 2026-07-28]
build_instructions/printed/stl/main body with optics-Filter holder D15mm.stl
22.0 x 12.8 x 31.0

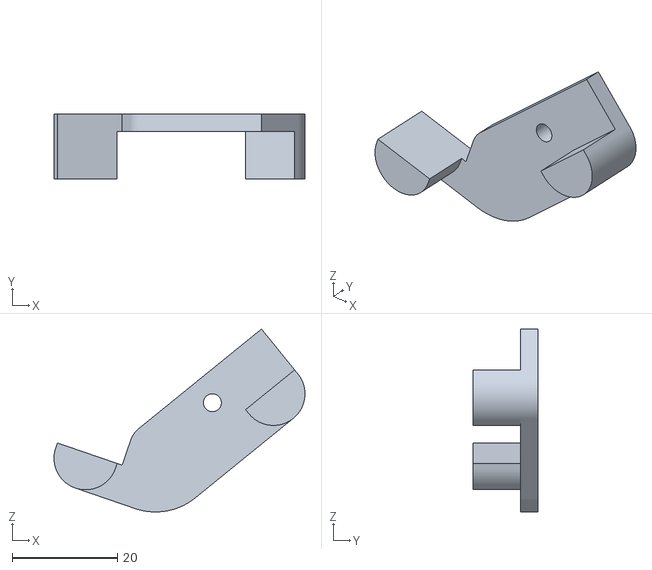
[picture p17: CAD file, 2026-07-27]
build_instructions/printed/stl/sample loader - assemblies-range limiter.stl
47.7 x 12.3 x 34.8

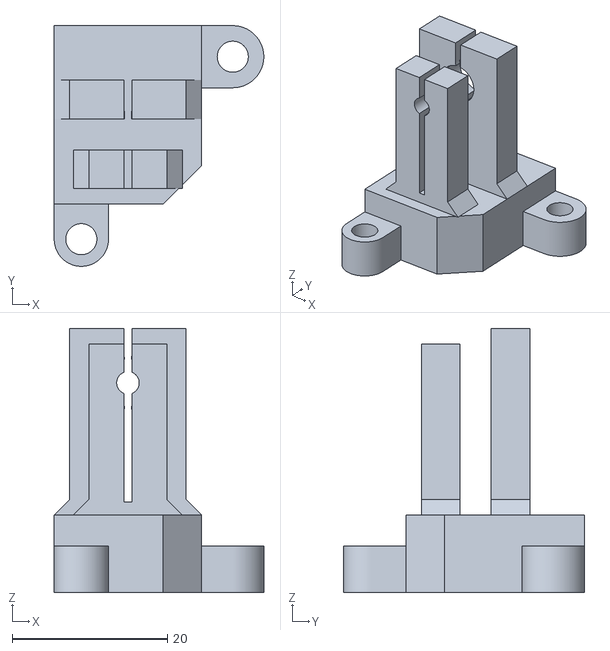
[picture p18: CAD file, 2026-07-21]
build_instructions/printed/stl/main body with optics-LED holder for FL+SSC testing.stl
27.0 x 31.0 x 34.0

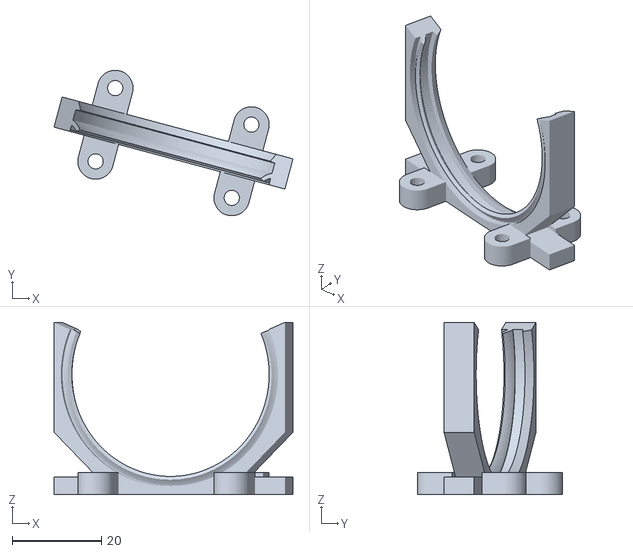
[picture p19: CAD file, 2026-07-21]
build_instructions/printed/stl/main body with optics-Holder spec foc lens.stl
53.6 x 32.6 x 38.7

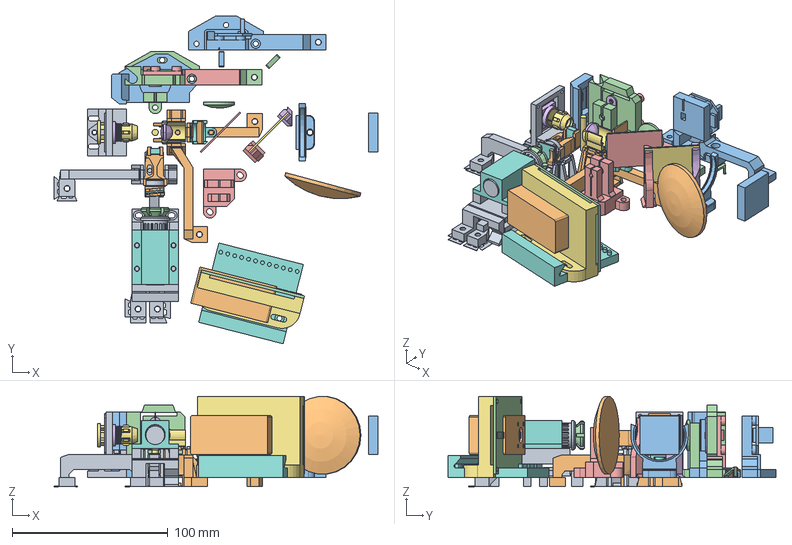
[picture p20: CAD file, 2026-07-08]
CAD and optical model/main body with optics - july broken.FCStd
208.0 x 210.3 x 58.0 mm
laser
Spectrum foc lens
Grating cube
PCB placeholder
laser collmating lens C775TMD-A - f = 4.0 mm, NA = 0.60, WD = 1.5 mm, Mounted Aspheric Lens, ARC: 350 - 700 nm
water
capillary quartz 4mm (round)
12X6mm Plano Convex Cylindrical Lens K9 Optical Glass Focal Length 27mm Center Thickness 4mm
Fused Silica 12.7mm Diameter Optical Plano Convex Lens Focal Length 50
corr cyl lens glass
SSC board
ssc foc lens f=50mm
dichroic filter 1
F8D12.7 aspherical condensing lens ACL 12708U CTN002243-E0W
dichroic filter 2
bandpass
2nd xy for laser focus lens
1st xy for condensing lens
cable stay
cable stay 2
dichroic holder 2a
dichroic holder 2b
Holder FL board
laser heat sink
lock nut
focusing lens holders
ssc holder
fsc (h slit) holder
fsc (h adjust) holder
fsc v slit 0.4mm
condensing lens holder
corr cyl lens holder
Holder Laser 25mW
fsc v slit 0.8mm
cg holder screw in
colimating lens adjustment tool - short
LED holder for FL+SSC testing
camera OV9726 25x30mm module
camera lens tube
test SiPM mount base
camera focus mount - v adjust
test PMT module (Hamamatsu H10723)
PDA10A holder v adjust
LED holder for FSC testing

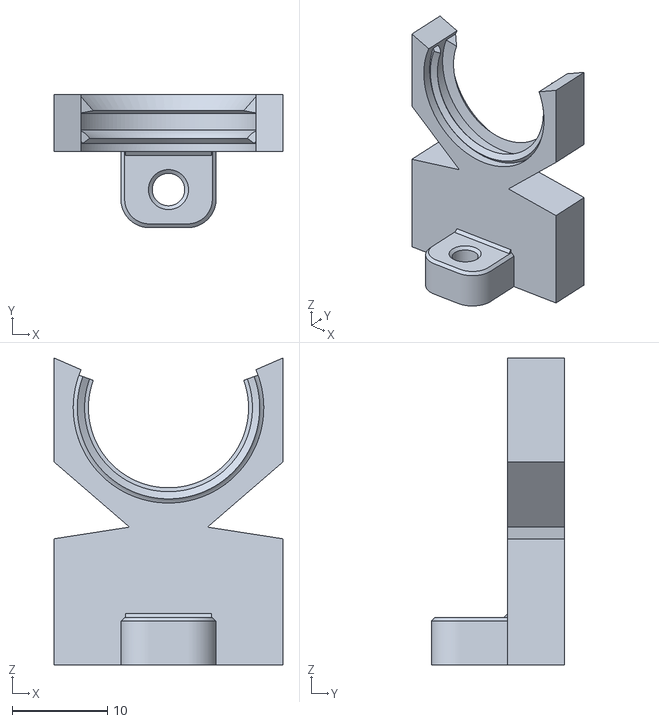
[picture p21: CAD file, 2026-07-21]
build_instructions/printed/stl/main body with optics-ssc foc lens holder.stl
24.0 x 14.0 x 32.2

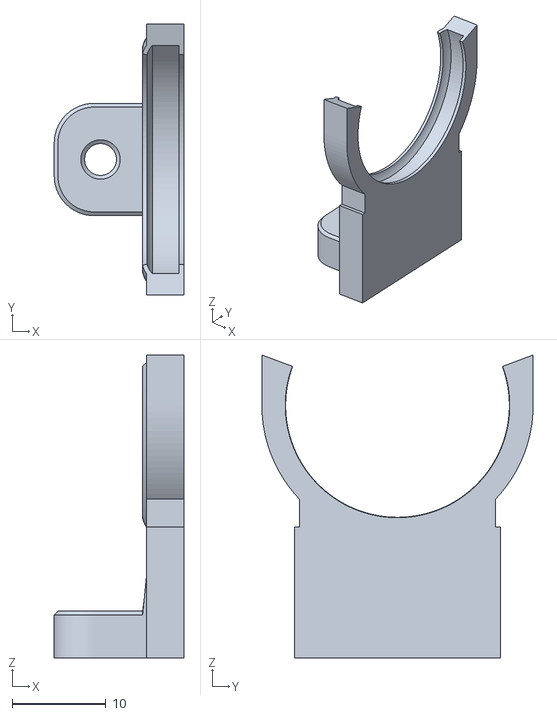
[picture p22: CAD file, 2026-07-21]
build_instructions/printed/stl/main body with optics-Filter holder D26mm.stl
13.8 x 29.0 x 32.4

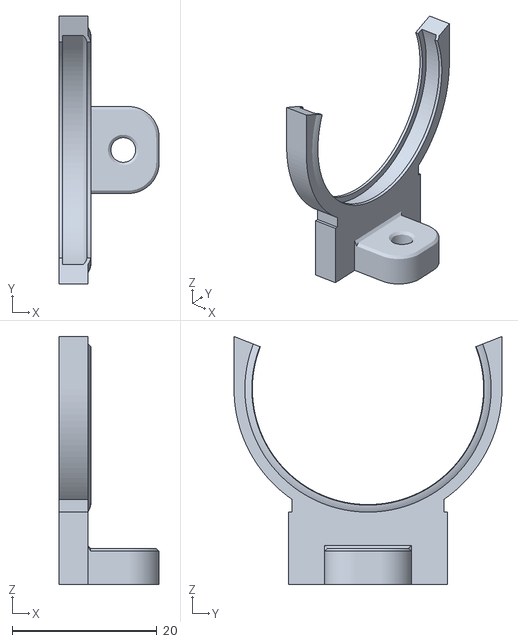
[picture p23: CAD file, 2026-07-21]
build_instructions/printed/stl/main body with optics-Filter holder D34mm.stl
13.8 x 37.0 x 34.2

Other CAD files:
CAD and optical model/Cytkit master assembly.FCStd
CAD and optical model/sample loader assembled.FCStd
CAD and optical model/sample loader - assembly flat.FCStd
CAD and optical model/Cytkit master assembly (Assembly4).FCStd
CAD and optical model/Cytkit master assembly (a2plus).FCStd
CAD and optical model/M10 fitting.FCStd
CAD and optical model/PCB exports/fsc board.FCStd
CAD and optical model/PCB exports/pumpcon.FCStd
CAD and optical model/PCB exports/sipm board.FCStd
CAD and optical model/base panel cover stand cart.FCStd
CAD and optical model/blower and housing.FCStd
CAD and optical model/case artwork.FCStd
CAD and optical model/cylindrical lens.FCStd
CAD and optical model/front panel logo relief.FCStd
CAD and optical model/main body with optics (square cuvette).FCStd
CAD and optical model/main body with optics - 5jun optics all ok.FCStd
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

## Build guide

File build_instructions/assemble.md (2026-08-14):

# Assemble the mechanics

## Attach base to stand {pagestep}

Lay the base and stand on their side as shown. The stand is attached to the base with 4 x [M3 self-tapping posi head screws 16 mm](mechanical/screws.yaml#self_tapping_m3x16_posi){qty:4, cat:mechanics}. 

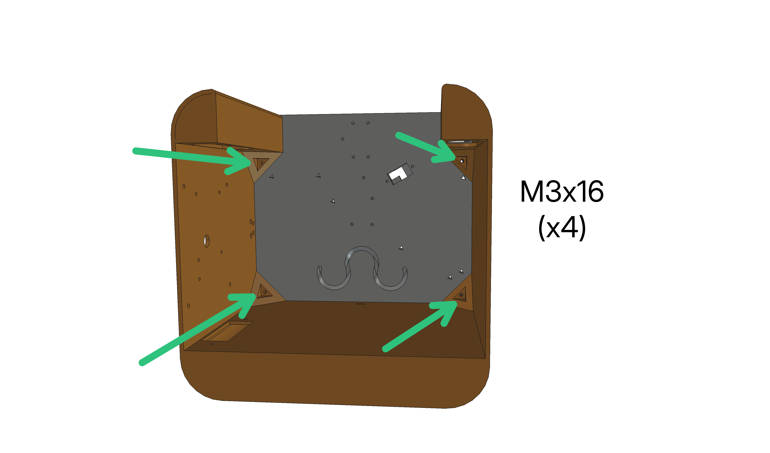
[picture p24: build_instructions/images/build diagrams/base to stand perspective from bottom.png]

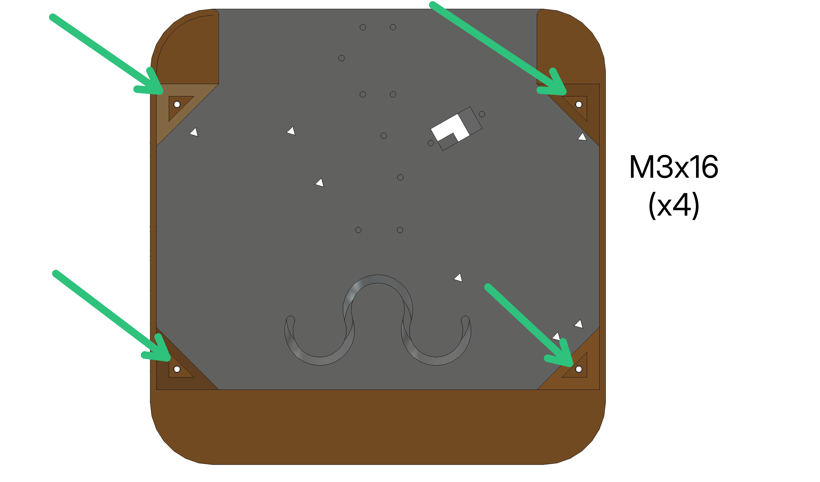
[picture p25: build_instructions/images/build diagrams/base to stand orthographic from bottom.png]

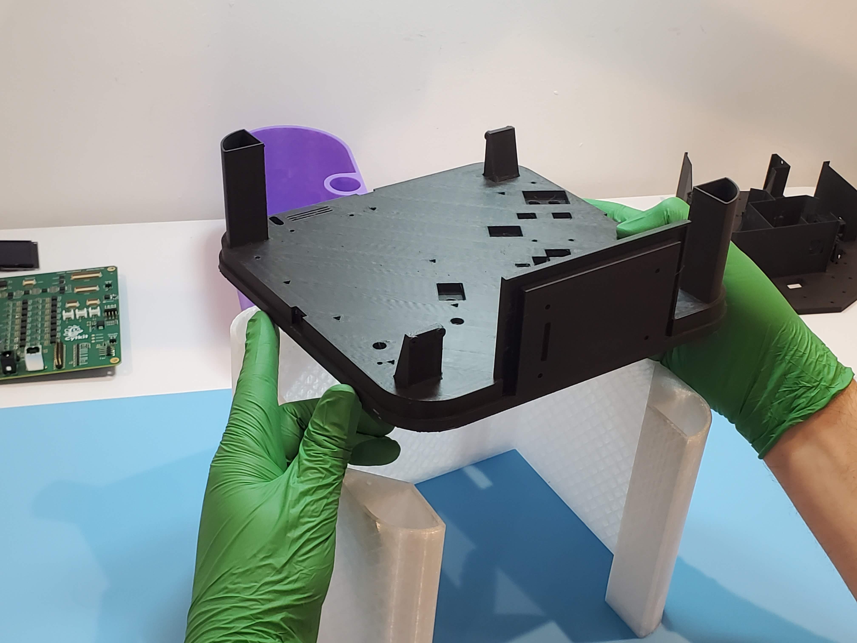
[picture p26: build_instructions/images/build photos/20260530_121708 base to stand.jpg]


## Attach main body to base, with springs under adjustment arms {pagestep}

First remove the printed brims on the ends of the adjustment arms of the main body as highlighted below.

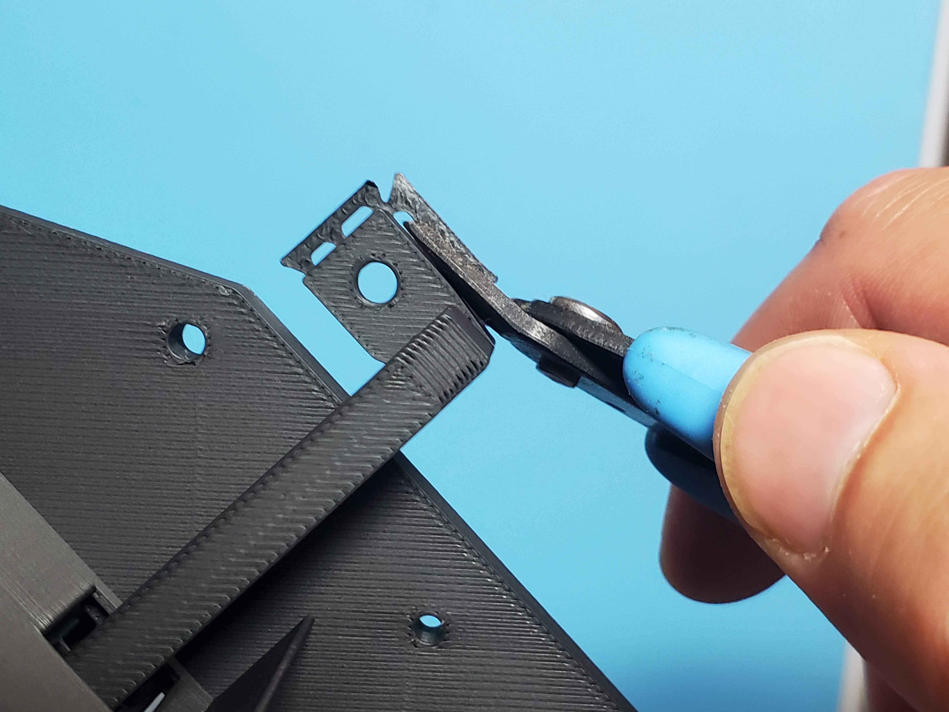
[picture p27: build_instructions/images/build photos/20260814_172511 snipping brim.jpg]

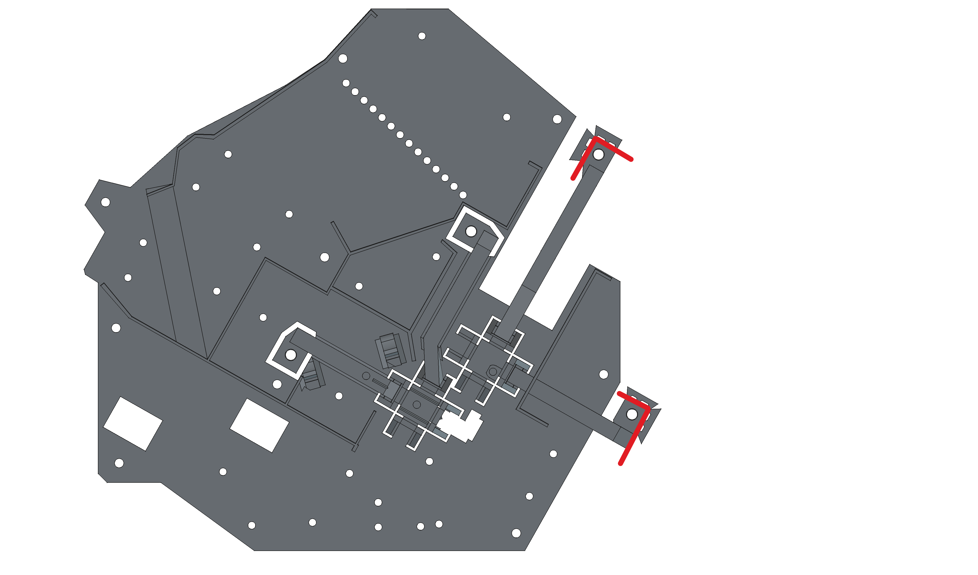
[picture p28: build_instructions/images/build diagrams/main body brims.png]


Stand the base and stand upright. Then stand 4x [Stainless steel compression springs, 0.5 mm wire, 20 mm length, 6 mm diameter](mechanical/springs_20x6x0.5mm.md){qty:4, cat:mechanics} into the circular recesses in the base as shown.

*** image of standing springs

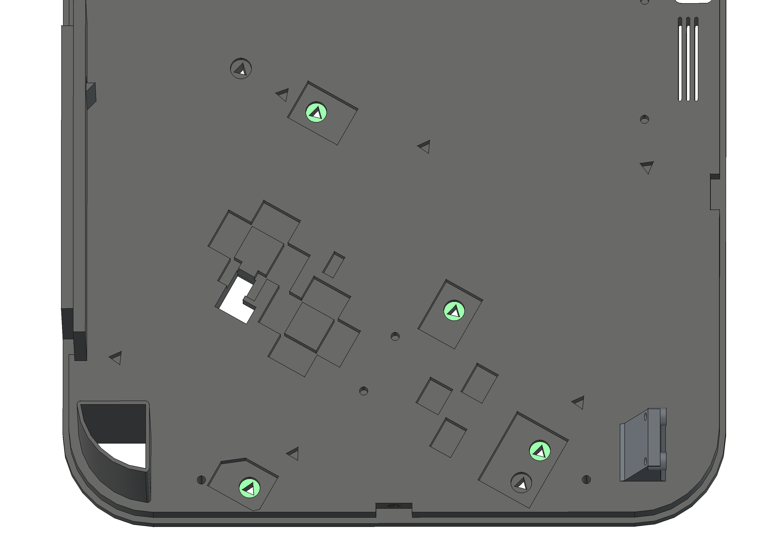
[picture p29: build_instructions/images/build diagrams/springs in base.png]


Carefully lower the main body onto the base as shown so that the circular cavities under the adjustment arms capture the top of the springs without knocking them over. Then screw the main body to the base with 9 x [M3 self-tapping posi head screws 12 mm](mechanical/screws.yaml#self_tapping_m3x12_posi){qty:9, cat:mechanics}. 

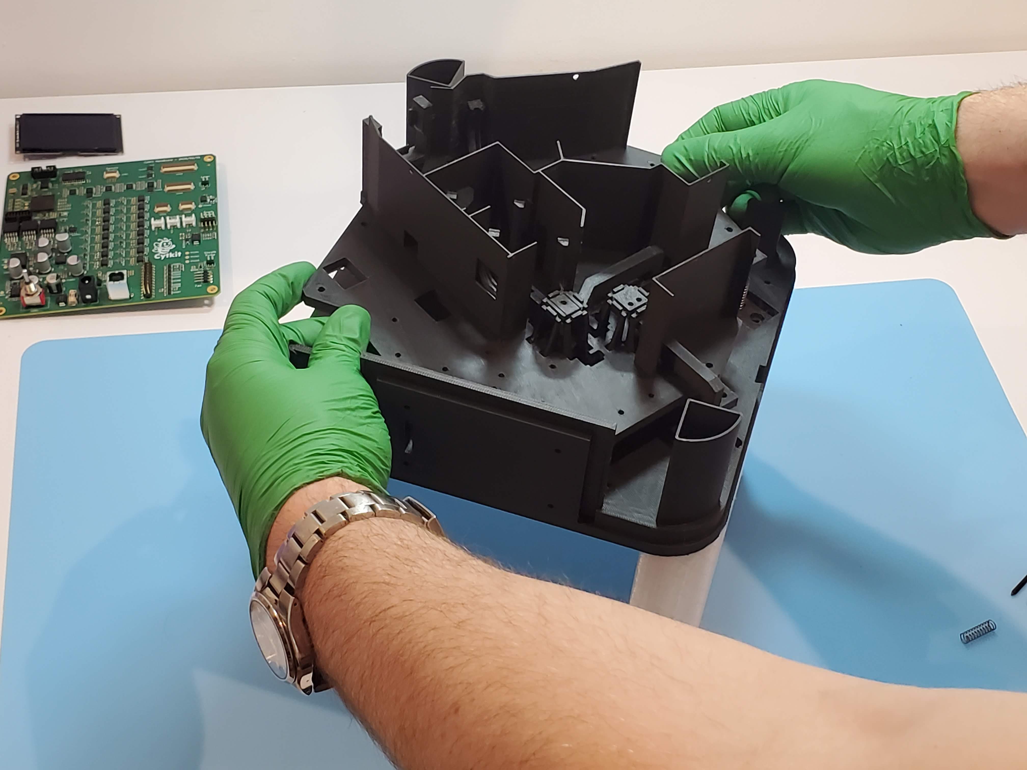
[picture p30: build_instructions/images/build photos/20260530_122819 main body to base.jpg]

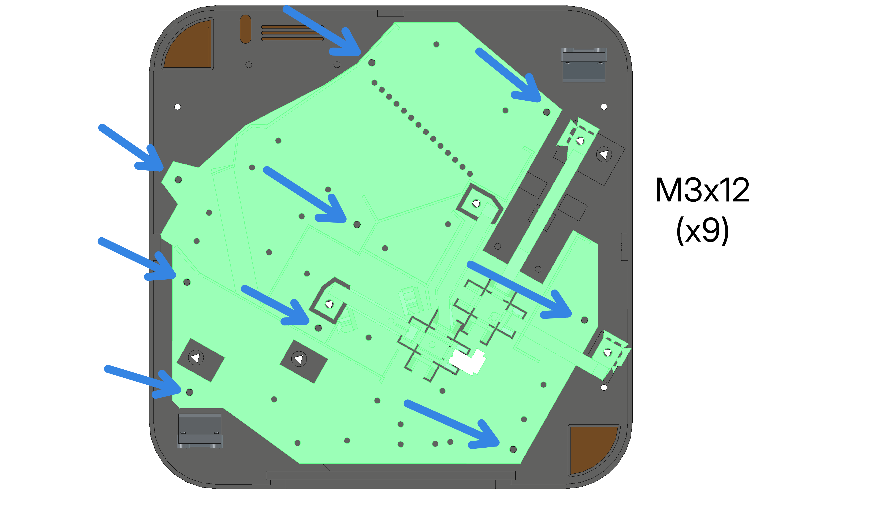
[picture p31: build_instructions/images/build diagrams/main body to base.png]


Screw in the 4 x [M3 self-tapping hex socket cap screws 25 mm](mechanical/screws.yaml#self_tapping_m3x25_hex_socket){qty:4, cat:mechanics}, first placing 1x [M3 washers](mechanical/screws.yaml#m3_washers){qty:1, cat:mechanics} under the screw head. These are the lead screws of the adjustment arms, one on each adjustment arm. Do not fully tighten. Screw them in so that the adjustment arms are horizontal and the xy flexure stages are centred.

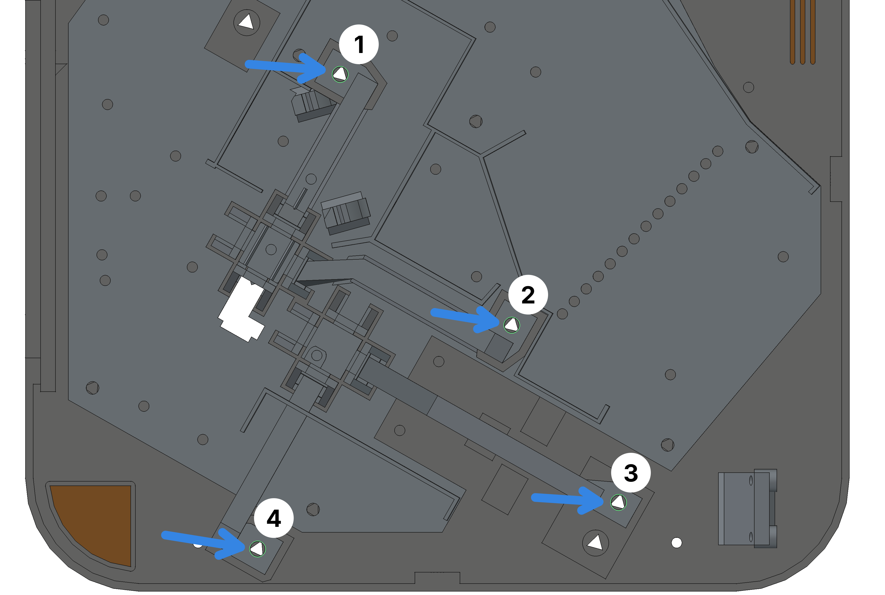
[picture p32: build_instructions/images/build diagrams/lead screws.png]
 
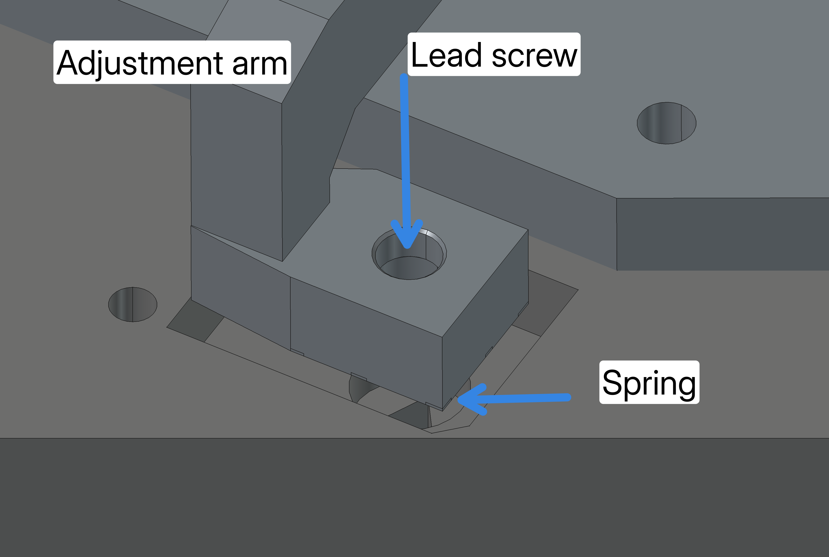
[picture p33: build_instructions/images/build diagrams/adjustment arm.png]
 
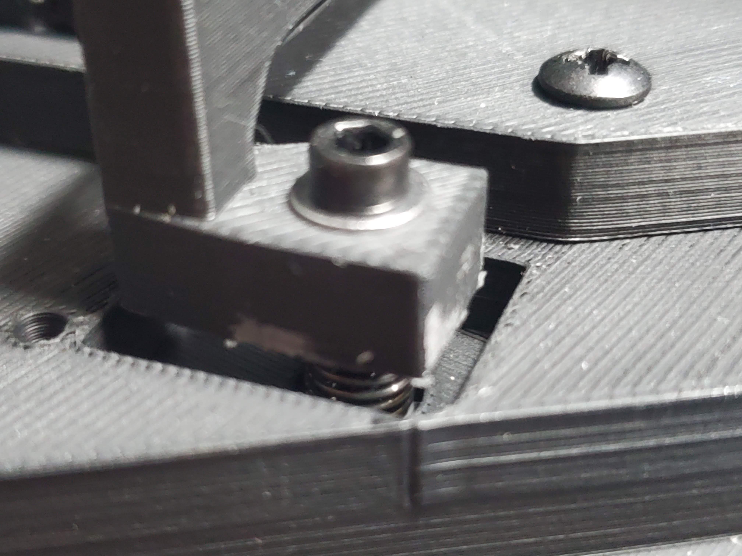
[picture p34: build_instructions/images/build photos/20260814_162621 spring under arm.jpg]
 
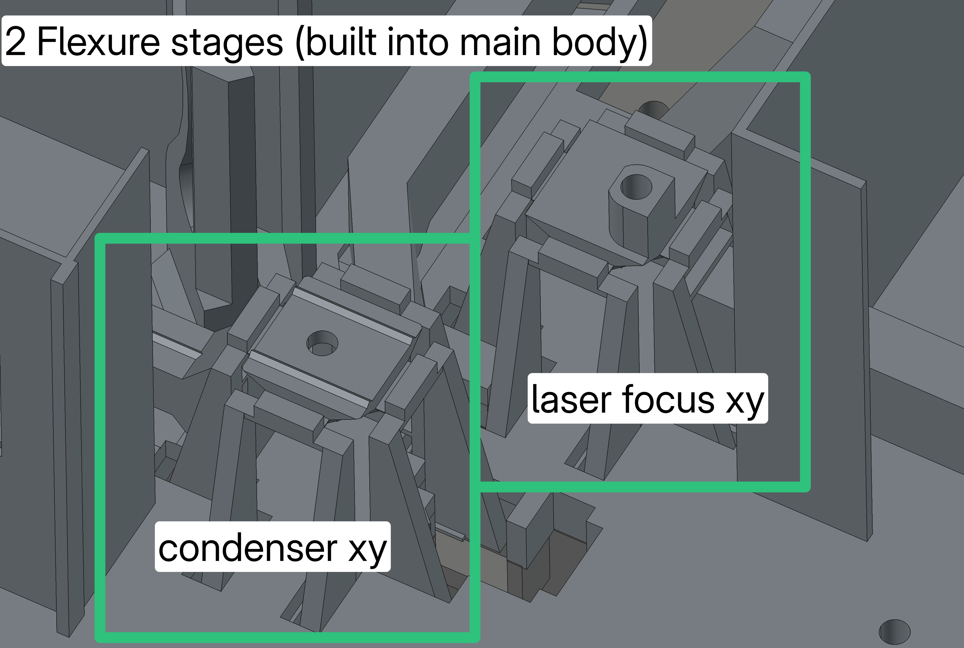
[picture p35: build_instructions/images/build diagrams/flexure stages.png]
 

## Attach fluidics cart to stand {pagestep}

Working underneath the instrument, you may lay the instrument on its side again if you find it easier. The fluidics cart is attached to the stand with 4 x [M3 self-tapping posi head screws 8 mm](mechanical/screws.yaml#self_tapping_m3x8_posi){qty:4, cat:mechanics}. 

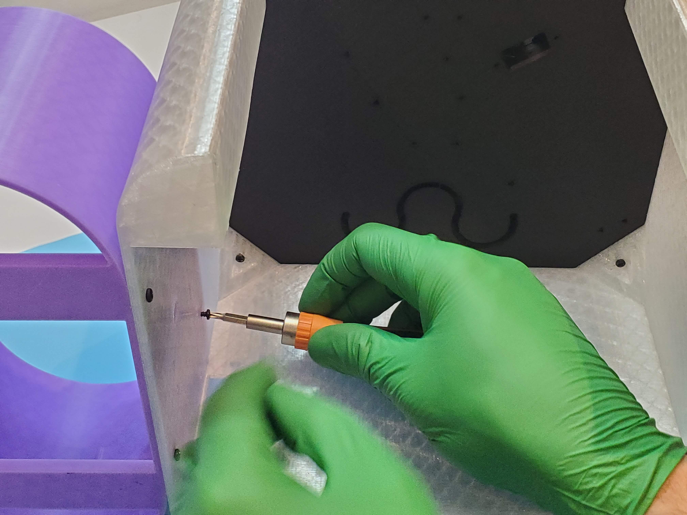
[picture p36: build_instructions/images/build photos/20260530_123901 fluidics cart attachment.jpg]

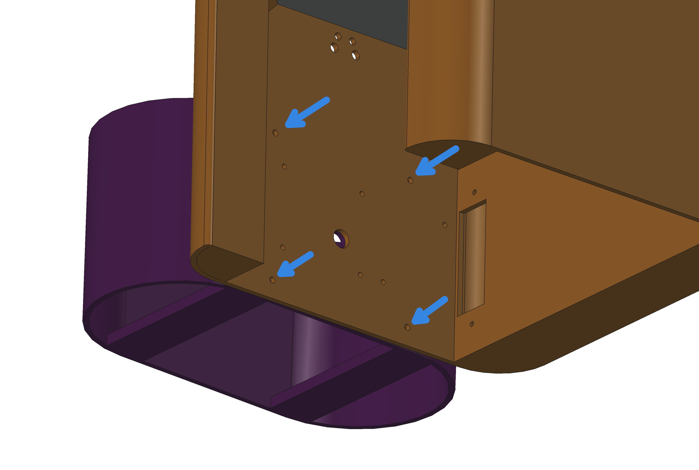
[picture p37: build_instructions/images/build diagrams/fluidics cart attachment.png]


## Instrument mechanics assembled

Your instrument should now look like this. 2 flexure xy stages should be adjustable with 4 lead screws. 

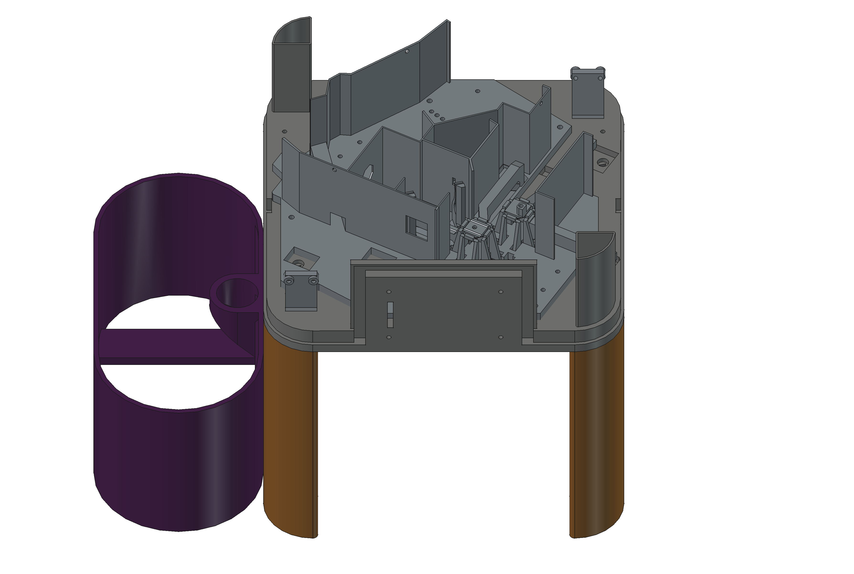
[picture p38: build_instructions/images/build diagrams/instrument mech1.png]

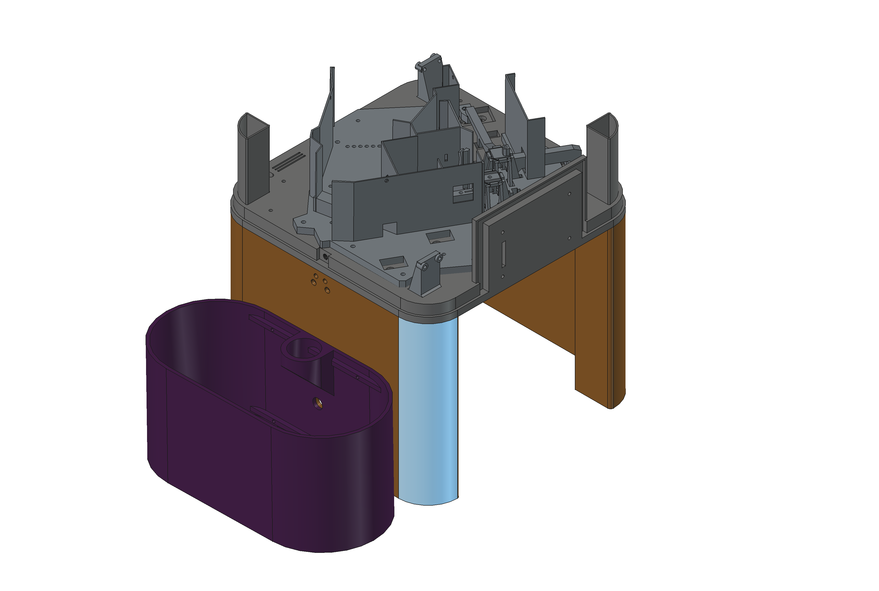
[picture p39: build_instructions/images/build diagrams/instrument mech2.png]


Now move on to assemble the fluidics!

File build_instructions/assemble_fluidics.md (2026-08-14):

# Assemble the fluidics

## Assemble flow cell {pagestep}

>! **Caution** 
>!
>! Take care not to damage sealing surfaces (barbs, o-ring grooves, o-rings, cuvette ends). Use plastic tweezers when holding o-rings (not fingers or metal tools).
>! 
>! Wear gloves to handle the cuvette: don't contaminate it with fingerprints.
>! 

First remove the printed supports from the flow cell. Take care not to damage the barb connectors.

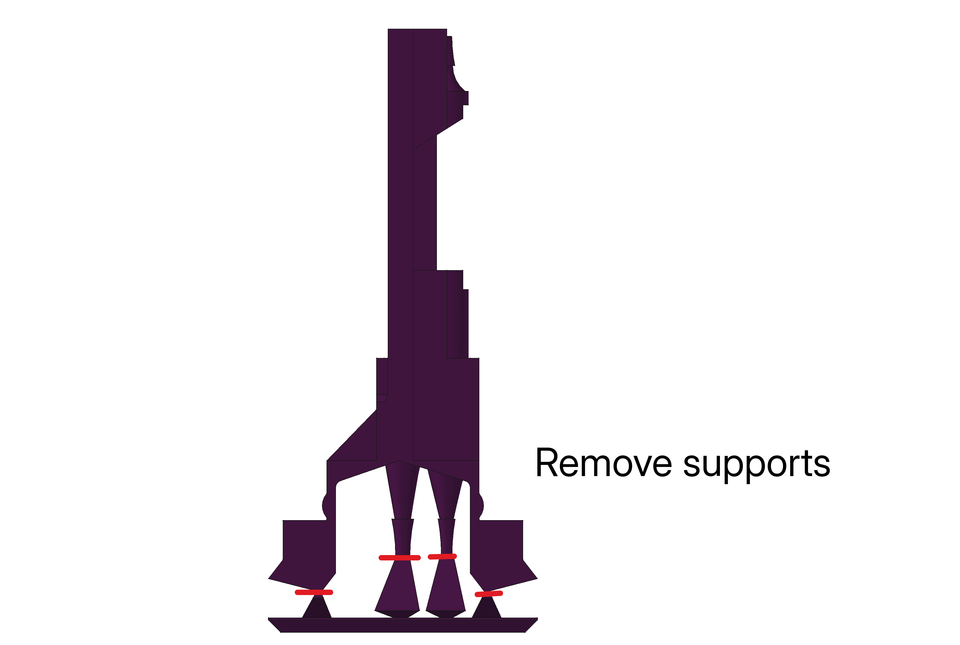
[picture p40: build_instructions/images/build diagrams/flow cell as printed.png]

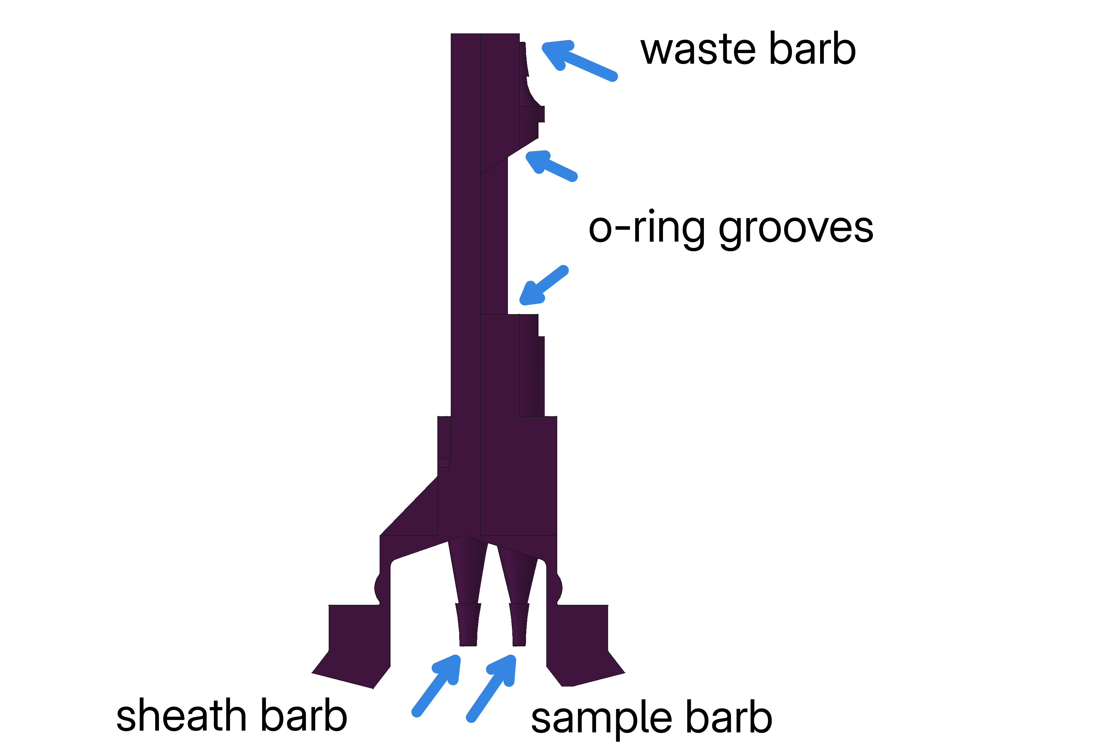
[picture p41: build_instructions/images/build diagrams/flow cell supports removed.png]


Second, insert the o-rings at either end within the o-ring grooves. If handled gently, the o-rings should stay inside the grooves, due to a slight printed overhang. 

Thirdly flex the flow cell slightly as shown below to insert the cuvette between the o-rings. Tip: if using a square cuvette, you should be able to see through the cuvette side (with a magnifying glass) that the o-ring is sealing against the surface.

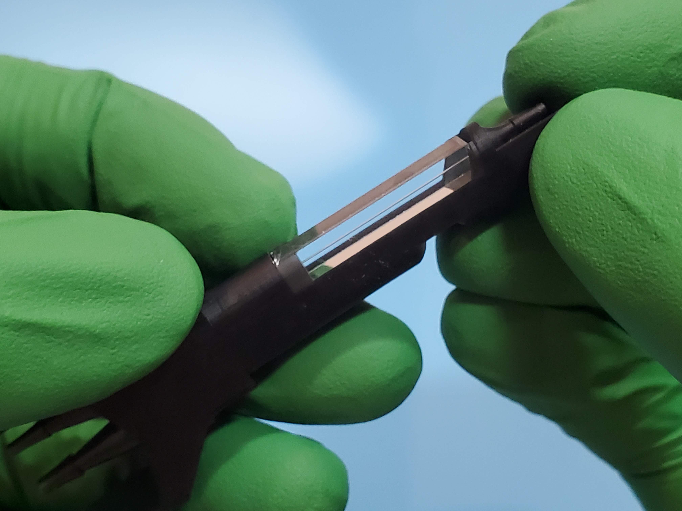
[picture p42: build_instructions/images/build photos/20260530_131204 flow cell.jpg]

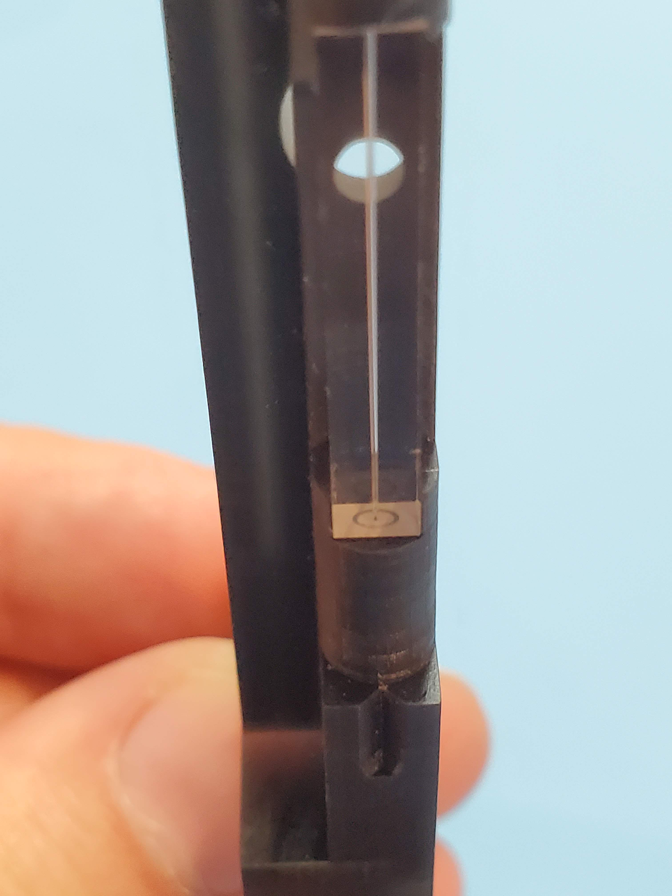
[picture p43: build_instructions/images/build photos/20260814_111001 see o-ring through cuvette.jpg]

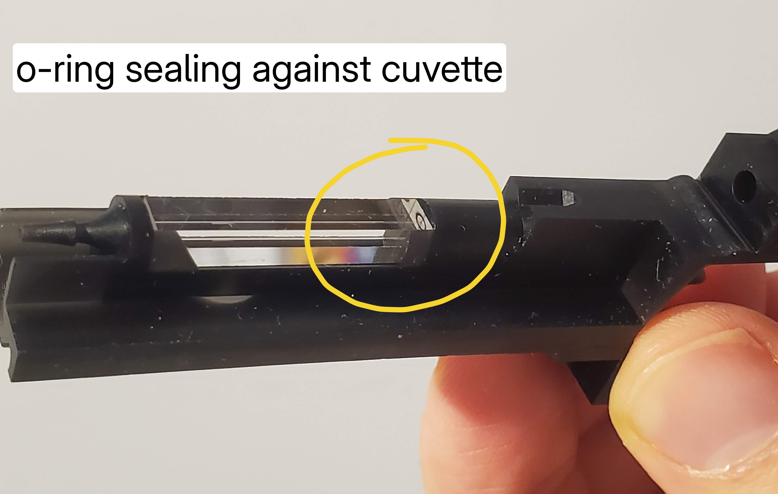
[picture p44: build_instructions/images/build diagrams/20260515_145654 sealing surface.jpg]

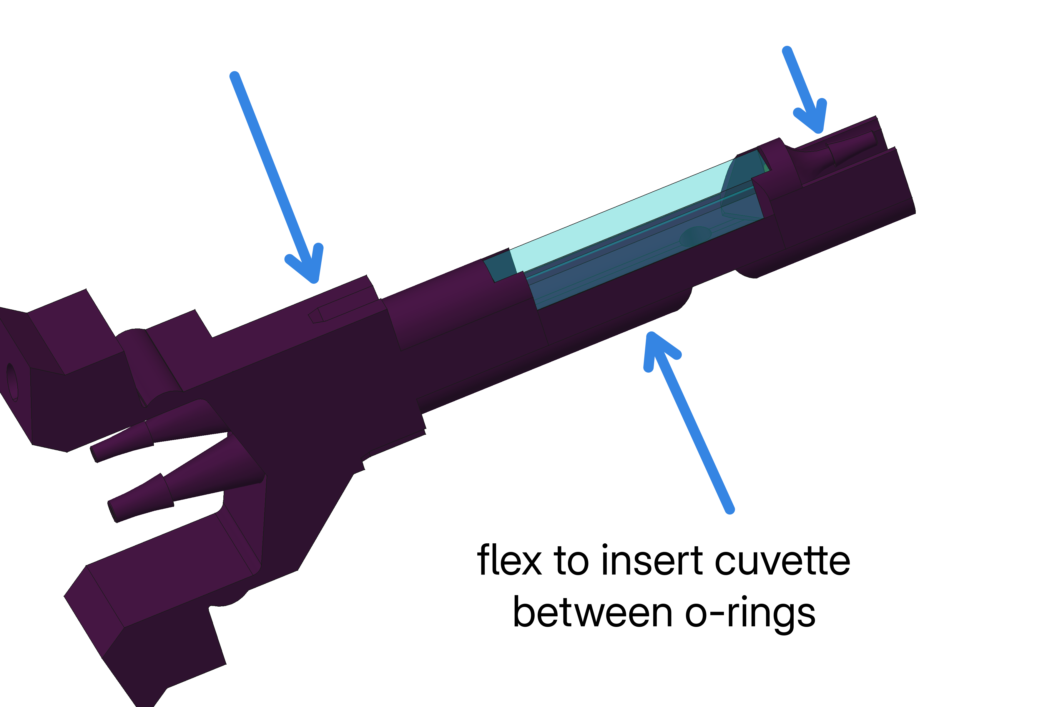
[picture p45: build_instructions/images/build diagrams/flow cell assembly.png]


Fourthly attach 120 mm of [Silicone tubing 2 mm OD 1 mm ID](fluidic/silicone_tubing_1mm.md){cat:fluidics} to the waste barb on top of the flow cell, and thread this tube through the duct on the side of the flow cell so it sticks out of the bottom.

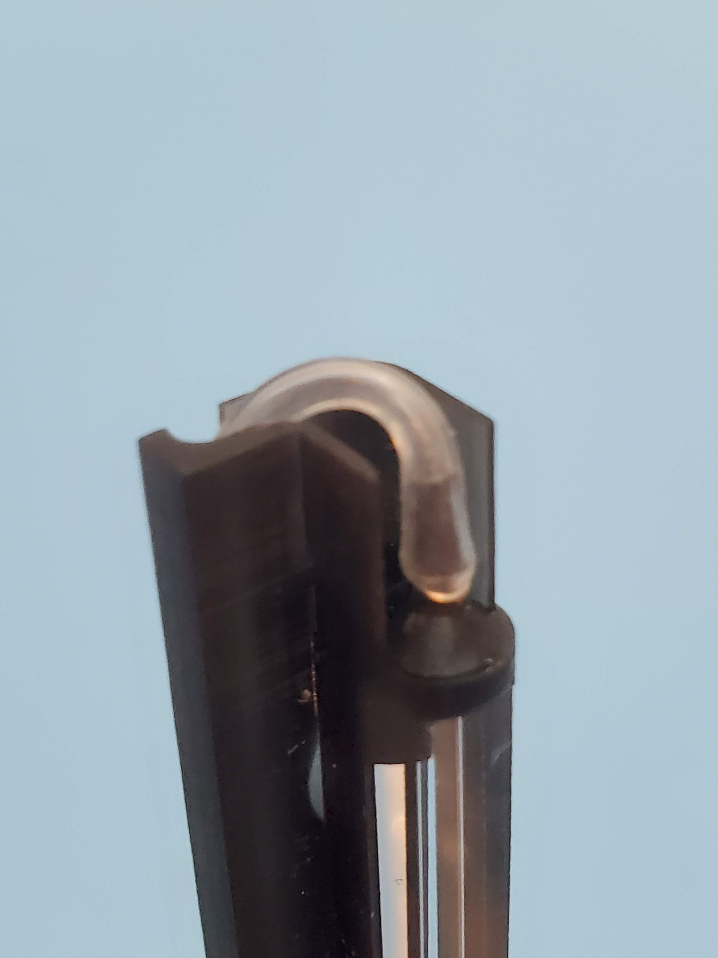
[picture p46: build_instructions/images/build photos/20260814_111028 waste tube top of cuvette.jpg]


Note how the flow cell works and how it will interface with the optics. Inside the flow cell is a sheath flow chamber with concentric sheath and sample inputs. The laser beam enters and leaves through opposite faces of the cuvette, with fluorescence (and SSC) collected by a condensing lens at 90 degrees, and a camera viewport for alignment opposite the condensing lens.

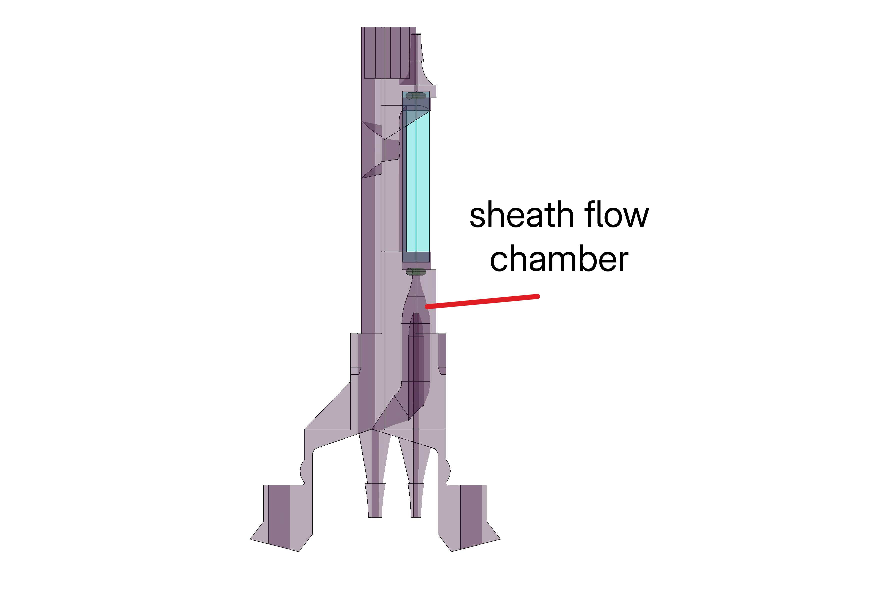
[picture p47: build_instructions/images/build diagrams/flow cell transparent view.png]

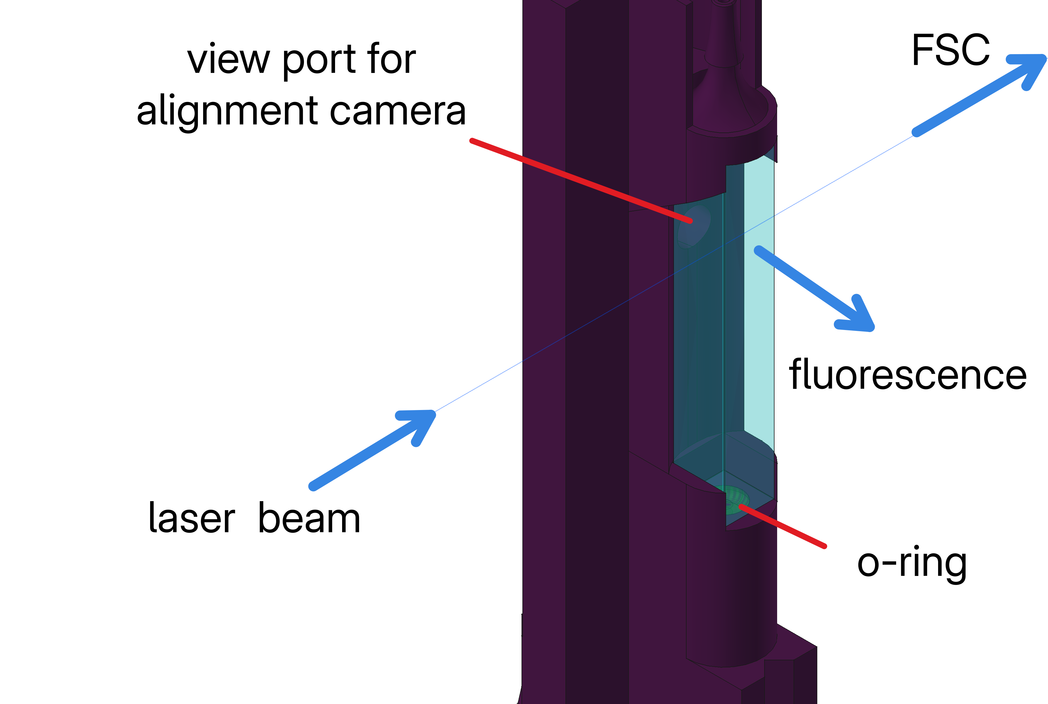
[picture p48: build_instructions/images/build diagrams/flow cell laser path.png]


## Prepare sheath and waste tank caps {pagestep}

The caps of the sheath and waste tanks must first be drilled with the right size holes to fit the required tubing connections. 

Note that the sheath flow is pulled by a vacuum on the wate bottle. Take care therefore to drill cleanly, especially the waste tank cap, as these holes must seal against a vacuum after fitting with connectors and tubing as follows.

**Sheath tank cap:**

1. 5 mm hole (sheath tube), 
1. 1.5 mm hole (vent)

**Waste tank cap:**

1. 3.5 mm hole (vacuum pump) 
1. 3.5 mm hole (pressure sensor or vent)
1. 3 mm hole (waste tube)

Attach the following fitings and tubing to the caps, threading them from inside the cap as follows:

**Sheath tank cap:**

1. [Bottom-of-bottle filter](fluidic/bottom_of_bottle_filter.md){qty:1, cat:fluidics} + 250 mm of [Silicone tubing 6 mm OD 4 mm ID](fluidic/silicone_tubing_4mm.md){cat:fluidics}; pass through 5 mm cap hole from inside to outside, then add
[Tube barb union 2.4x6.4](fluidic/tube_barb_union2.4x6.4.md){qty:1, cat:fluidics}.

**Waste tank cap:**

1. For waste stream: 50 mm of [Silicone tubing 2 mm OD 1 mm ID](fluidic/silicone_tubing_1mm.md){cat:fluidics} + [Tube barb union 1.6x2.4](fluidic/tube_barb_union1.6x2.4.md){qty:1, cat:fluidics}; pass through 3 mm cap hole from inside to outside, then add 480 mm of [Silicone tubing 2 mm OD 1 mm ID](fluidic/silicone_tubing_1mm.md){cat:fluidics}.
1. For pressure sensor or vent: [Tube barb union 1.6x3.2](fluidic/tube_barb_union1.6x3.2.md){qty:1, cat:fluidics} + 400 mm of [Silicone tubing 3.2 mm OD 1.6 mm ID](fluidic/silicone_tubing_1.6mm.md){cat:fluidics}; pass through 3.5 mm cap hole from inside to outside.
1. For vacuum pump: [Tube barb union 1.6x3.2](fluidic/tube_barb_union1.6x3.2.md){qty:1, cat:fluidics} + 400 mm of [Silicone tubing 3.2 mm OD 1.6 mm ID](fluidic/silicone_tubing_1.6mm.md){cat:fluidics}; pass through 3.5 mm cap hold from inside to outside.

In the waste tank cap, push the tube barbs from the inside into the holes in the cap so that they seal. Screw the caps on both bottles. You can then put 2x cable ties on the bundle of tubing coming out of the waste bottle at 50 mm intervals to keep them tidy.

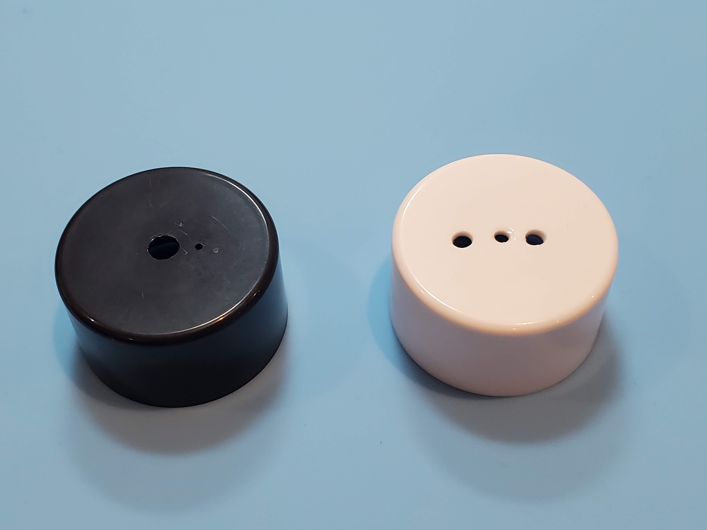
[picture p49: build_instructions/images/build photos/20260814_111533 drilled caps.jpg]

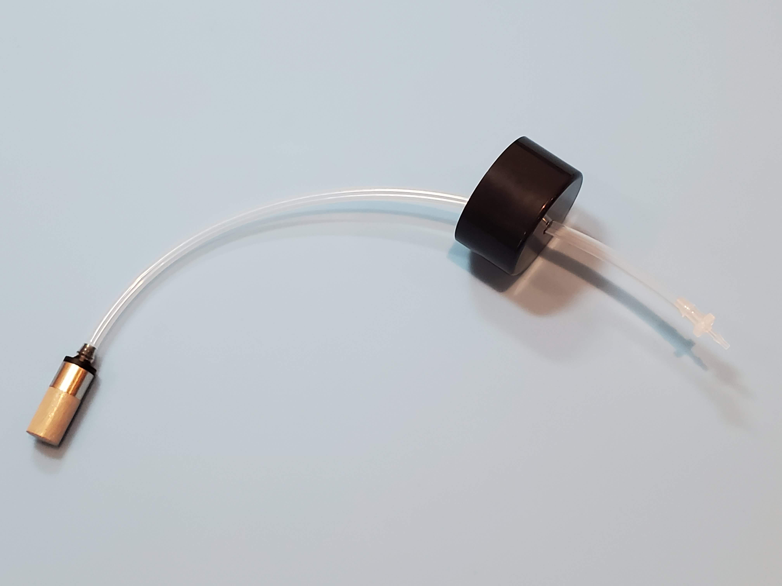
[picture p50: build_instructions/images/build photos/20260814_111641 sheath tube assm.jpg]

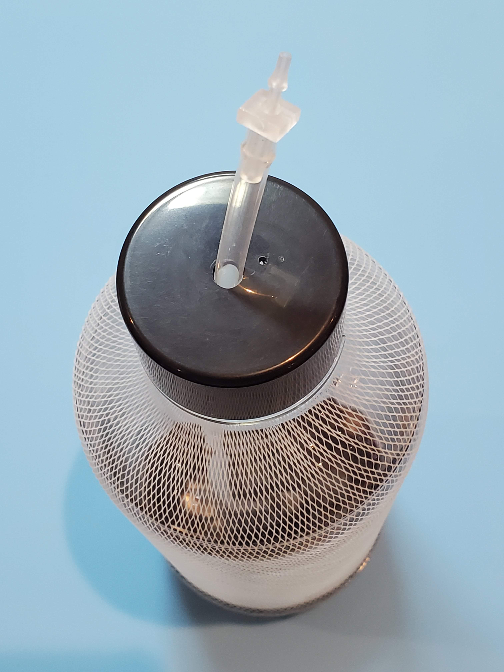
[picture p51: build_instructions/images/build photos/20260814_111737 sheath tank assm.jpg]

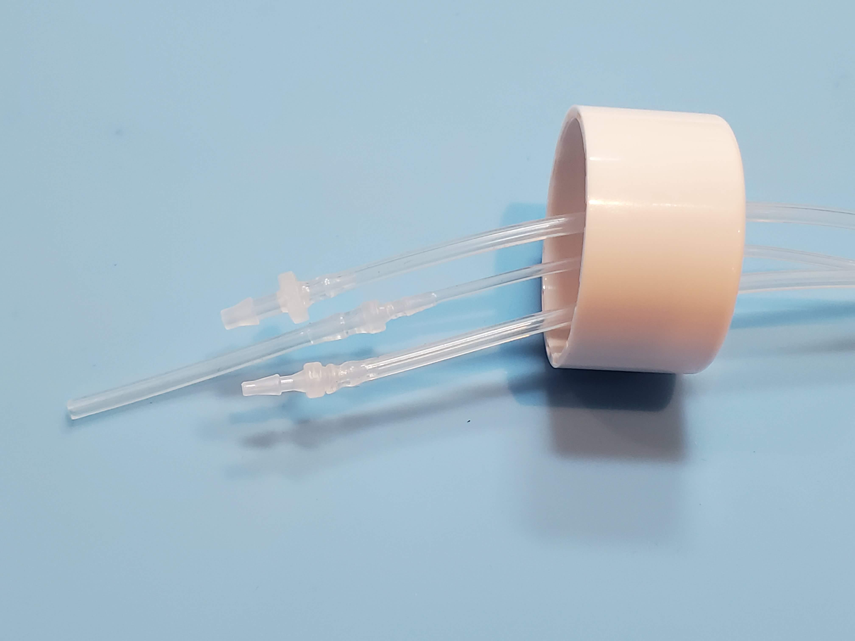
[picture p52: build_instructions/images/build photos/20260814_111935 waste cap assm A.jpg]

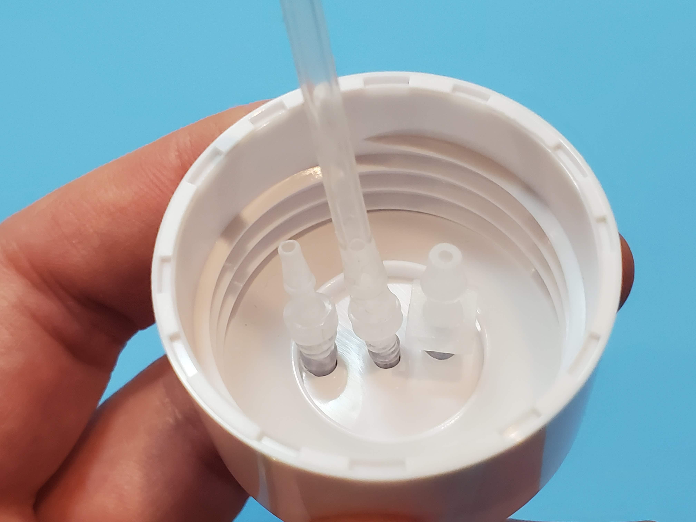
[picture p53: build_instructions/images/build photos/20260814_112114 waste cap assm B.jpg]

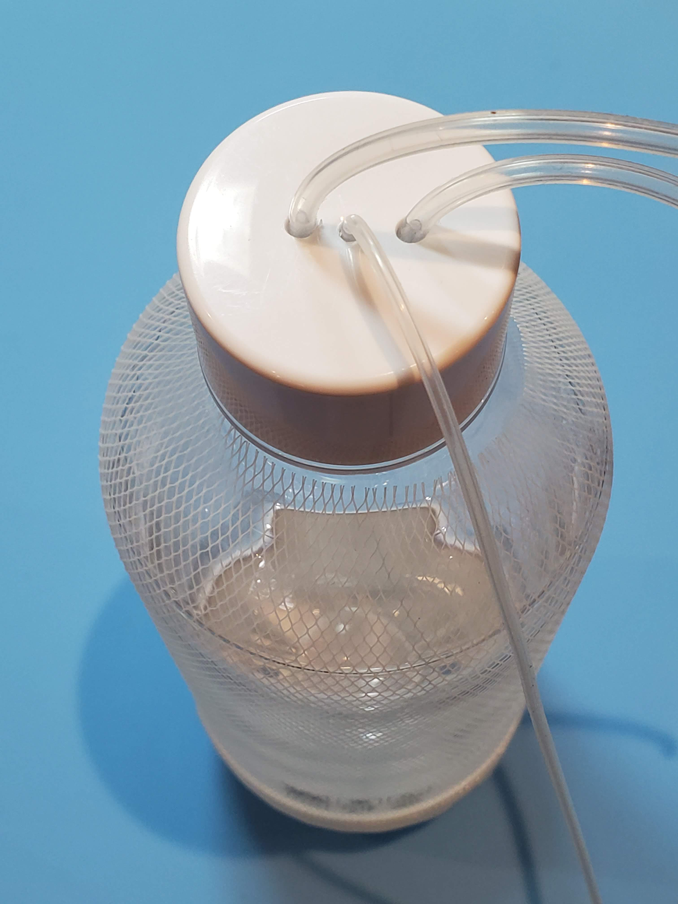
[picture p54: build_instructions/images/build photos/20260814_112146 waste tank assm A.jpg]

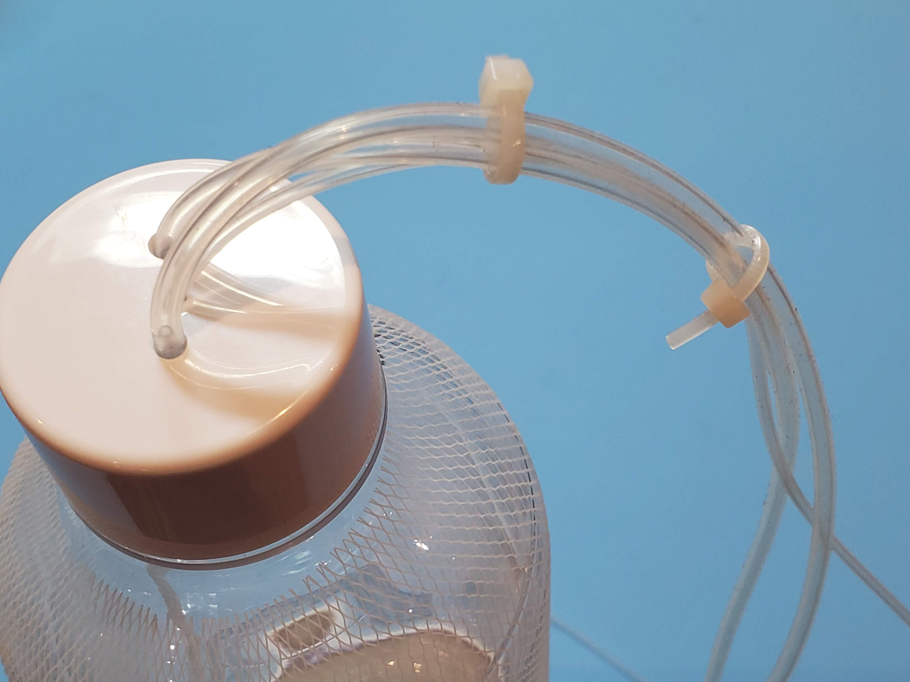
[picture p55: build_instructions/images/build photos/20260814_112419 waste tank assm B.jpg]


## Prepare and assemble sample loader  {pagestep}

The sample loader is a linkage of several mechanical bodies that are printed in a single piece. Before using, it must be loosened and lubricated. 

To loosen the hinges, apply pressure to the two sets of adjacent hinges as shown. The outer hinges down and the middle hinge up. Alternate between the two sets. If printed well, very little pressure applied with the fingers should be required to loosen the hinges. Once the linkage is loose, add light lubricating oil to the hinges. Then work the linkage back and forth repeatedly until it can move with very little friction. 

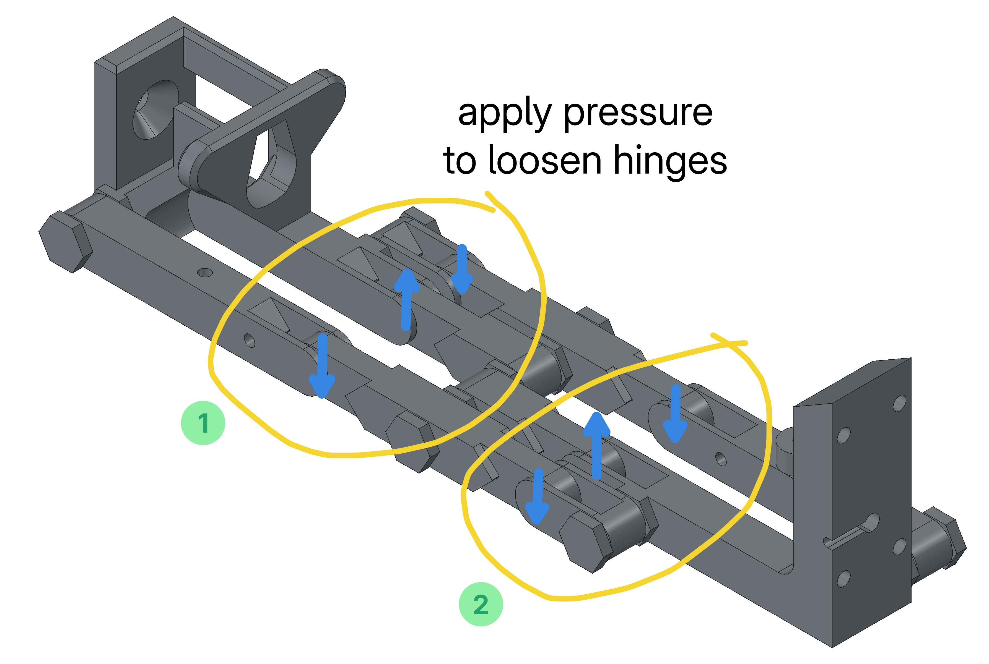
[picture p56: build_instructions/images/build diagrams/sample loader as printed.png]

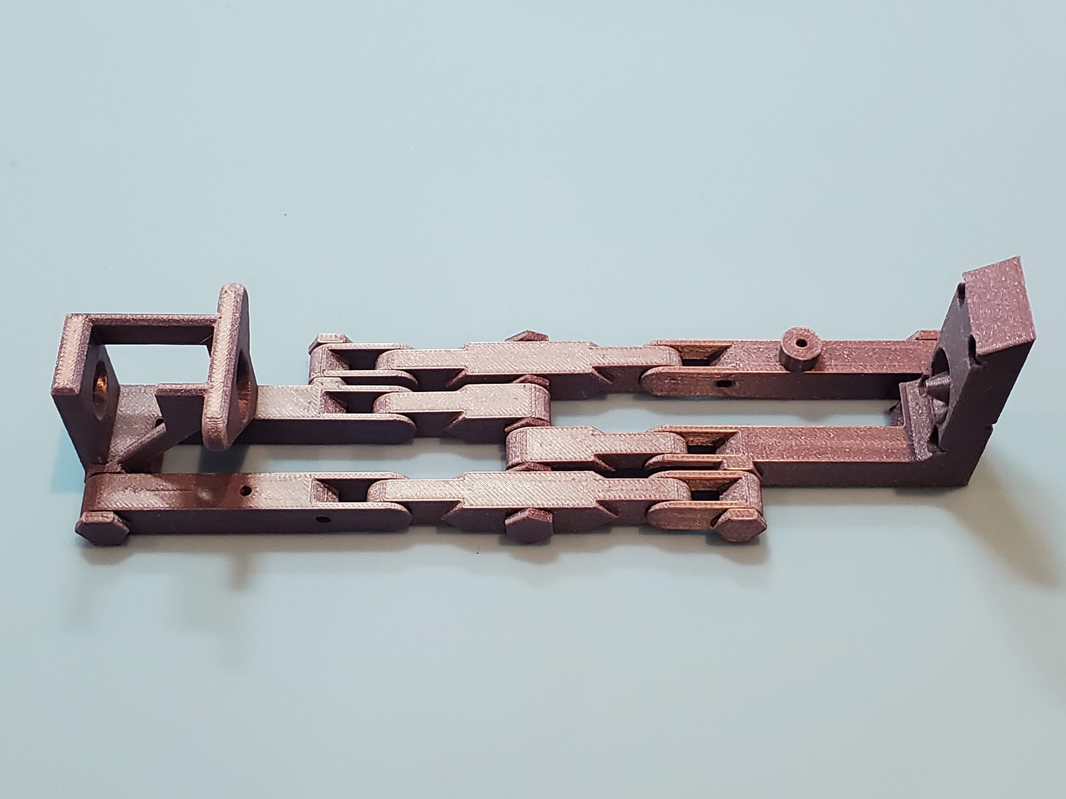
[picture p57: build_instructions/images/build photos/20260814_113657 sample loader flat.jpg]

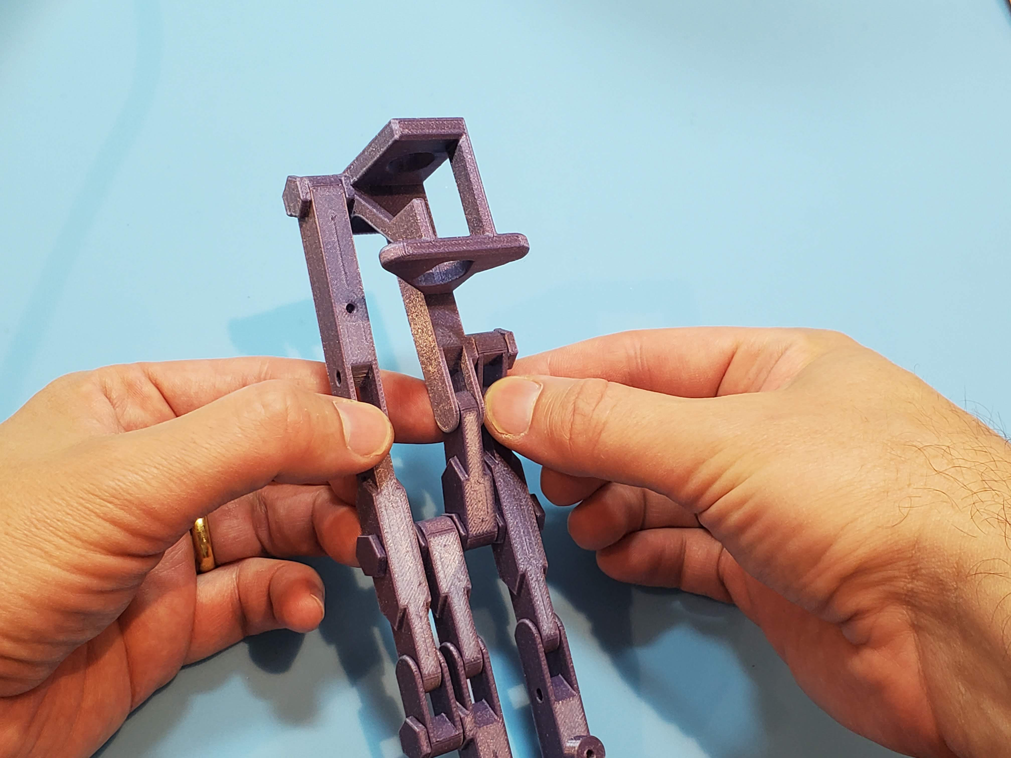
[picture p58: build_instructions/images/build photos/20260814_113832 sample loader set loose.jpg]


<video width="640" height="360" controls>
  <source src="images/build photos/20260814_113858 flex sample loader lubricate.mp4" type="video/mp4">
  Your browser does not support the video tag.
</video>

Attach the two sample loader range limiters to the holes as shown using 2x [M3 self-tapping posi head screws 8 mm](mechanical/screws.yaml#self_tapping_m3x8_posi){qty:1, cat:mechanics}.

Attach the sample loader retaining spring ([Stainless steel extension springs, 0.3 mm wire, 20 mm length, 6 mm diameter](mechanical/extension_springs_20x6x0.3mm.md){qty:1, cat:mechanics}) with a 1x [M3 self-tapping posi head screws 8 mm](mechanical/screws.yaml#self_tapping_m3x8_posi){qty:1, cat:mechanics}.

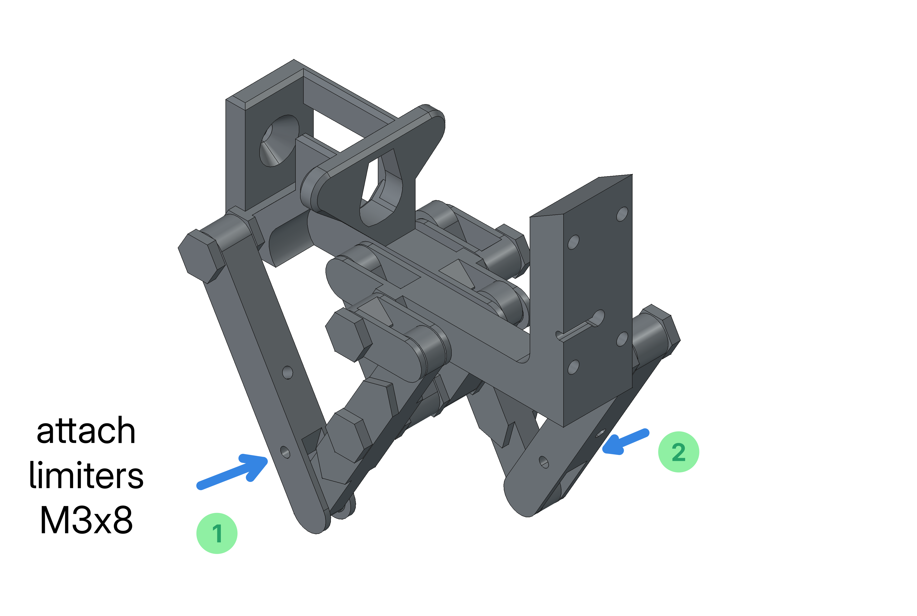
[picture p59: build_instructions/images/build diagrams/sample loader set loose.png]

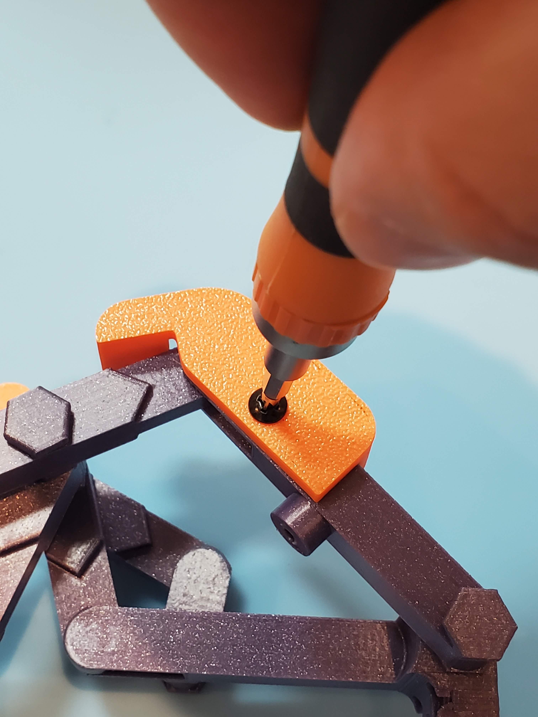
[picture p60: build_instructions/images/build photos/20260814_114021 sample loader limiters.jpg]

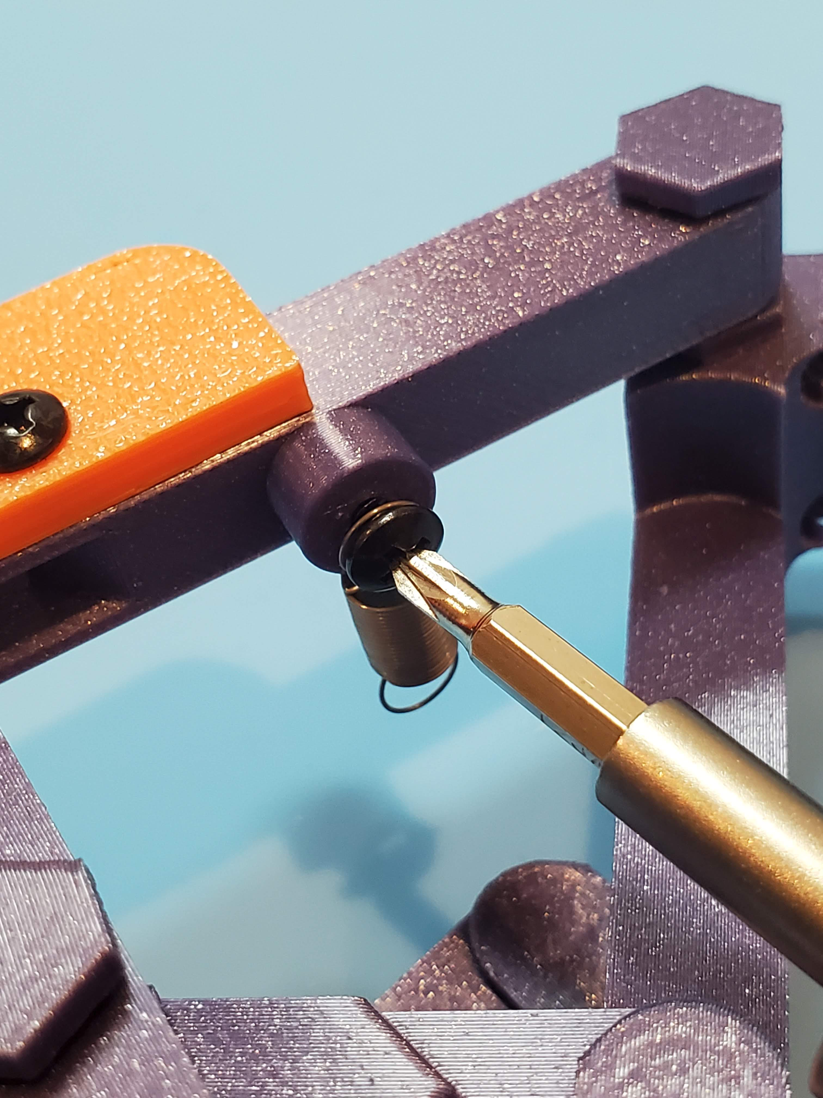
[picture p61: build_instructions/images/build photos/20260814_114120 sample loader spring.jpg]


Finally, check that the SIP tube will fit in the sample loader: you may need to carefully ream the hole with a 1.6 mm drill bit. The SIP tube is a 78 mm length of [Peek tubing 1.6mm OD 0.25mm ID](fluidic/peek_tubing.md){cat:fluidics}. Cut the required length, straighten it if it was supplied curved, and gentle push it into the hole provided.

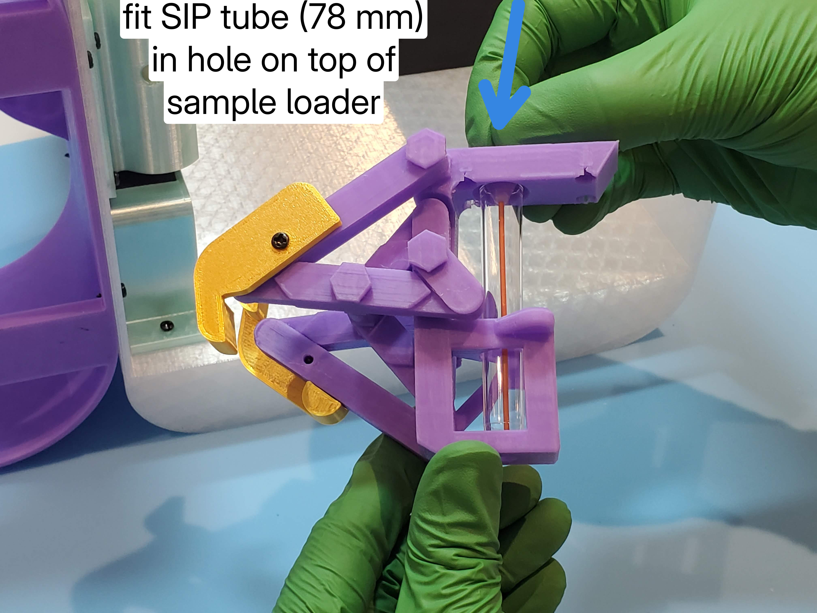
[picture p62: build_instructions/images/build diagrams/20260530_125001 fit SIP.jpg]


>i **How the sample loader works** 
>i
>i The sample loader is based on a [Kempe Kite Inversor 2](https://www.thingiverse.com/thing:7035940) which is a parallel line linkage: it allows a single degree of freedom, while keeping the SIP and sample tube parallel to each other.
>i
>i 

## Prepare sample (peristaltic) pump assembly  {pagestep}

First fit the barb connectors to the peristaltic pump tubing.

>? **Help Block** 
>?
>? if no barb connectors were supplied with your pump, these can be substituted with 10 mm sections of [Peek tubing 1.6mm OD 0.25mm ID](fluidic/peek_tubing.md){qty:1, cat:fluidics}.

If building the Cytkit 2S-14F, fit the stepper motor connector board to the pump, and ribbon cable to the stepper motor connector board.

Then fit the following tubing to the sample pump:

1. For flow cell sample inlet: 20 mm of [Silicone tubing 2 mm OD 1 mm ID](fluidic/silicone_tubing_1mm.md){cat:fluidics}.
2. For SIP tube: 55 mm of [Silicone tubing 2 mm OD 1 mm ID](fluidic/silicone_tubing_1mm.md){cat:fluidics}.
3. SIP tube itself (as described above).

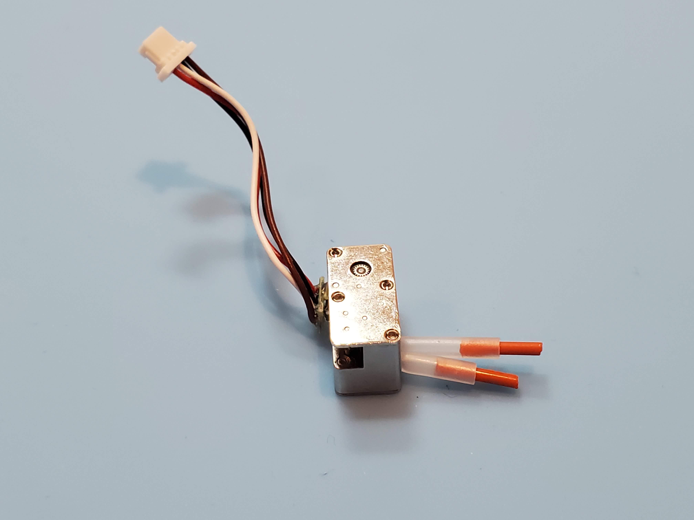
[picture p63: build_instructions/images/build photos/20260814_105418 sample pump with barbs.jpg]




## Prepare sheath (vacuum) pump assembly  {pagestep}

If building the Cytkit 1S-1F configuration, first cut 2 x 200 mm wires for positive and neutral connections to the vacuum pump. Solder on end of each to the vacuum pump terminals. Leave the other ends as bare wire to connect to the screw terminals of the motor controller. 

>i If building the Cytkit 2S-14F configuration, the vacuum pump is already supplied with the correct length of wires and a connector to attach to the main board

Place the pump body in the sheath pump holder (flexible printed part). Then cut 90 mm of  [Silicone tubing 6 mm OD 4 mm ID](fluidic/silicone_tubing_4mm.md){cat:fluidics} and put on the end a [Tube barb union 2.4x6.4](fluidic/tube_barb_union2.4x6.4.md){qty:2, cat:fluidics}.




## Attach tubing to flow cell {pagestep}

Now attach the following:

1. The flow cell sample inlet barb to the open tubing on the sample pump.
1. A barb connector (or 10 mm length of [Peek tubing 1.6mm OD 0.25mm ID](fluidic/peek_tubing.md){qty:1, cat:fluidics}) on the end of the waste tube coming from the flow cell.
1. 470 mm of [Silicone tubing 2 mm OD 1 mm ID](fluidic/silicone_tubing_1mm.md){cat:fluidics} on the flow cell sheath inlet barb.





## Attach fluidics system to instrument {pagestep}

Insert the flow cell through the hole in the bottom of the base, and screw it tight with 2x [M3 self-tapping posi head screws 16 mm](mechanical/screws.yaml#self_tapping_m3x16_posi){qty:1, cat:mechanics}.





Put the sample pump holder over the sample pump and fasten with 1x [M3 self-tapping posi head screws 8 mm](mechanical/screws.yaml#self_tapping_m3x8_posi){qty:1, cat:mechanics}.



Thread the SIP tube into the sample loader and attach the sample loader to the base with 4x [M3 self-tapping posi head screws 16 mm](mechanical/screws.yaml#self_tapping_m3x16_posi){qty:1, cat:mechanics}. Make sure the flexible tube from the SIP sits in the groove on top of the sample loader and is not pinched by fastening the sample loader.




Fasten the retaining spring with 1x [M3 self-tapping posi head screws 10 mm](mechanical/screws.yaml#self_tapping_m3x10_posi){qty:1, cat:mechanics}.



If building the Cytkit 2S-14F configuration, screw on the sample pump connection board with 2x [M3 self-tapping posi head screws 8 mm](mechanical/screws.yaml#self_tapping_m3x8_posi){qty:1, cat:mechanics}. 



Screw on the sheath pump holder to the inside of the stand (left hand side) with 2x [M3 self-tapping posi head screws 10 mm](mechanical/screws.yaml#self_tapping_m3x10_posi){qty:1, cat:mechanics}.



Connect tubing:

1. Thread the sheath and waste tubing through the respective top holes in the left hand side of the stand. 
1. Connect the sheath tubing to the barb at the end of the sheath tank assembly. 
1. Connect the waste tubing to the barb hanging from the flow cell waste outlet.
1. Thread the pump tubing from the waste tank through the front hole of the second row of holes in the left hand side of the stand, and connect it to the barb coming out of the vacuum pump assembly.
1. If building the Cytkit 2S-14F configuration, thread the pressure sensor tubing from the waste tank through the remaining hole in the second row of holder in the left hand side of the stand.
1. If building the Cytkit 1S-1F configuration, insert a 30 mm section of [Peek tubing 1.6mm OD 0.25mm ID](fluidic/peek_tubing.md){cat:fluidics} in the waste tank vent tubing.
1. Thread the dangling sheath and waste tubes through the serpentine retaining groove.





## Attach fan holder to stand {pagestep}

These instructions are for the Cytkit 2S-14F only:

1. Insert the blower fan in its printed holder.
1. Route the fan cable, the sheath pump cable and the pressure sensor tubing through the hole in the left rear of the stand to the electronics compartment behind it.
1. Screw on the fan holder
1. Check that the cables emerge at the rear of the stand (in the electronics compartment).






## Test and check the fluidics

Make sure SIP tube reaches the bottom of a sample tube placed in the sample loader. 



Make sure the sample loader goes up and down smoothly, stays stably at both the top and bottom positions, and that a sample tube can be inserted and removed easily. You may need to straighten the PEEK SIP tube by bending it in the opposite direction from whichever way it naturally curled.

<video width="640" height="360" controls>
  <source src="images/build photos/20260814_122227 test sample loader compressed.mp4" type="video/mp4">
  Your browser does not support the video tag.
</video>

You have now build the fluidics system and are ready to build the optics!

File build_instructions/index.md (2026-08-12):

# Cytkit

Cytkit is an open-source spectral cytometer. You can make your own, either from a kit or by sourcing all the parts yourself. All mechanical parts are designed to be 3D-printed. You can also study and modify the design in free software (FreeCAD, with an ray-tracing optical model in the FreeCAD Optical Workbench).

The Cytkit instrument comprises: one laser, beam-shaping optics, a fluidic system with sheath flow and pumps for sample and sheath, optics for collecting and filtering emitted light, a dispersion element to split the emission into a spectrum, and [flexural degrees of freedom](https://doi.org/10.1364/BOE.385729) to align the laser beam and align the emission to detectors. 
 
# Cytkit configurations

You can configure your Cytkit with various detectors and acquisition electronics. These instructions cover two configurations as follows. 

## Cytkit 1S-1F

Cytkit 1s-1f fully assembled

This is the 1-scatter 1-fluorescence configuration, which uses electronics from test equipment vendors: 1 x amplified photodiode ([Thorlabs PDA10](components/thorlabs_pda10.md){qty:1, cat:electronics1S1F}), 1 x PMT ([Hamamatsu H10732](components/hamamatsu_H10732.md){qty:1, cat:electronics1S1F}, 1 x USB oscilloscope ([Picoscope 5000 Series](components/picoscope.md){qty:1, cat:electronics1S1F}), as well as separate boards for motor control, and power supplies. 

>i Note that 1 fluorescence detector is pretty minimal for a spectral system, to make an understatement! (At least you can mount it at a wavelength of your choice.) Moreover, the USB oscilloscope can only transfer a low rate of events. This configuration is intended as an demonstration for education and technology development, rather than as a useful cytometer.

## Cytkit 2S-14F 

Cytkit 1s-1f fully assembled

This is the 2-scatter 14-fluorescence configuration, which uses the [Astute Devices Cytometry Electronics Kit](components/cytometry_electronics_kit.md){qty:1, cat:electronics2S14F} (2x photodiode board, 1x SiPM array board, 1x main board, 1x pump connector board, 2x interlock switches, 1x blower fan, 1x OLED display, 1x power supply, 1x set of cables). 

This configuration is intended as an easy way to build your own fully functional spectral cytometer. 

>i The Astute Devices Cytometry Electronics Kit is in development and anticipated to be released in Q4 2026.

# Safety first

>!! Cytkit uses a Class 3B laser (a 488 nm laser diode with output power of approximately 25 mW). This is hazardous to the eyes. We strenuously advise you to have laser safety training before building your own Cytkit. 

Suitable laser safety glasses that block 488 nm light are included in the bill of materials.

At no point should you switch on the laser unless it is contained within the main body of the Cytkit instrument with the beam blocked by the FSC detector.

The coarse alignment step in the build instructions requires working with an exposed beam (cover off). You should take safety precautions for this step: 

* check for stray reflections 
* wear laser safety goggles that block 488 nm light 
* ensure that no other people are likely to be exposed to the laser, for example by being in the same environment. 

The fine alignment and operational use of the instrument are with the beam enclosed (cover on). 

Two interlocks are provided in the Astute Devices Cytometry Electronics Kit to switch off the laser if the cover is removed.

# Build Instructions

You will need the parts according to the [bill of materials]{BOM} according to which configuration you are building. You will also need the following tools:

* a set of Allen/hex keys
* a set of precision screwdrivers

Unless you have purchased a kit, you will need the following in addition:

* an FDM 3D printer (for almost all mechanical parts)
* a resin 3D printer (for a few precision parts including fluidic sealing parts)

To align and test the instrument, you will need:

* bright fluorescein beads 5 um diameter (or any size less than 20 um) 
* rainbow calibration beads (e.g. Spherotech RCP-30-5A or Bangs Quantum 8-Peak)
* fluorescein solution (optional)

1. [Print the mechanical parts](print_parts.md){step}
1. [Source the remaining components](source_parts.md){step}
1. [Assemble the mechanical parts](assemble.md){step}
1. [Assemble the fluidics](assemble_fluidics.md){step}
1. [Assemble the optics](assemble_optics.md){step}
1. [Install the electronics](electronics.md){step}
1. [Install and run the software](software.md){step}
1. [Coarse alignment](coarse_alignment.md){step}
1. [Fine alignment](fine_alignment.md){step}
1. [Test your Cytkit cytometer](test_cytometer.md){step}

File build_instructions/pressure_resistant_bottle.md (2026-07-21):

---
PartData:
    Specs:
        Material: xyz
    Suppliers:
        XYZ Ltd Inc:
            PartNo: xyz
            Link: 'xyz'
---
# Source part

Description.

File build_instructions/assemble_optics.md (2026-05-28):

# Assemble the optics

*** picture of optics before assembly

## Insert spectrum focusing lens {pagestep}

## Insert SSC focusing lens  {pagestep}

## Insert coloured glass filter  {pagestep}

## Insert dichroic filters  {pagestep}

## Insert condensing lens {pagestep}

## Assemble beam shaping assembly  {pagestep}

## Assemble laser module  {pagestep}

## Assemble camera module  {pagestep}

## Mount detectors  {pagestep}

### Cytkit model 1S-1F

### Cytkit model 2S-14F

*** picture of optics in main body after assembly

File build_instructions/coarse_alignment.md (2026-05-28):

# Coarse alignment

## Safety check {pagestep}

## Power on laser {pagestep}

## Coarse laser collimation {pagestep}

*** screenshot camera image
*** pic beam on

## Attach laser focus assembly {pagestep}

*** pic attached

## Flow fluorescecein solution {pagestep}

*** pic flow, video from cam

## Laser focus / collimation coarse adjustment {pagestep}

## Mount fluorescence screen {pagestep}

## Align laser (coarse) {pagestep}

## Align collection (coarse) {pagestep}

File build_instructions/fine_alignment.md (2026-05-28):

# Fine alignment

## Mount fluorescence detector {pagestep}

## Flow alignment beads {pagestep}

## Align laser (fine) {pagestep}

## Align fluorescence collection (fine) {pagestep}

## Align SSC collection {pagestep}

## Align FSC collection {pagestep}

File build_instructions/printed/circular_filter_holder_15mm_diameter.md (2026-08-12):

---
PartData:
    Specs:
        Design output: main body with optics-Filter holder D15mm.stl
        Material: PLA+ (Black)
        Print orientation: upright

---
# Circular filter holder (15 mm diameter)

Push-in holder for a circular filter or lens, e.g. 15 mm ND filter.



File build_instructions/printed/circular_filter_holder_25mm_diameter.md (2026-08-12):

---
PartData:
    Specs:
        Design output: main body with optics-Filter holder D26mm.stl
        Material: PLA+ (Black)
        Print orientation: upright or flat

---
# Circular filter holder (25 mm diameter)

Push-in holder for the circular filters: coloured glass longpass filter and dichroic longpass filter.



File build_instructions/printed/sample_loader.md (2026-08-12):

---
PartData:
    Specs:
        Design output: sample loader - assembly flat.stl
        Material: PLA+, any colour
        Print orientation: flat

---
# Sample loader

Print-in-place mechanical linkage sample loader, based on a Kempe Kite Inversor 2 design. Takes 5 mL FACS tubes, Eppendorf tubes, etc.



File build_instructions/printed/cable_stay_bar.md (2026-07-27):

---
PartData:
    Specs:
        Design output: base panel cover stand cart-cable stay bar.stl
        Material: Matt Black PLA / HyperPLA / UltraPLA
        Print orientation: upright

---
# Cable stay bar

Allows the ribbon cables to be neatly routed as they go between the electronics compartment and the optics compartment.



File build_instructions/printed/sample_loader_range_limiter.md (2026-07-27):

---
PartData:
    Specs:
        Design output: sample loader - assemblies-range limiter.stl
        Material: PLA+, any colour
        Print orientation: flat

---
# Sample loader range limiter

Limits the range of motion of the sample loader to stop it being over-extended or folding the wrong way. Two required. 



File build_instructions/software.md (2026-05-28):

# Install and run the software

## Install Honeychrome  {pagestep}

## Install Picoscope software (Cytkit model 1S-1F only)  {pagestep}

## Connect to hardware and run Honeychrome  {pagestep}

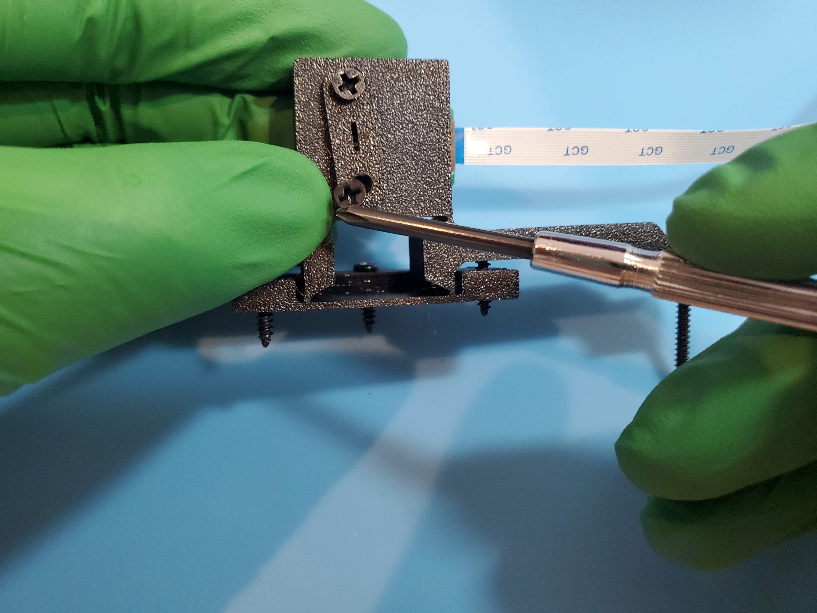
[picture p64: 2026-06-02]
build_instructions/images/build photos/20260530_152505.jpg

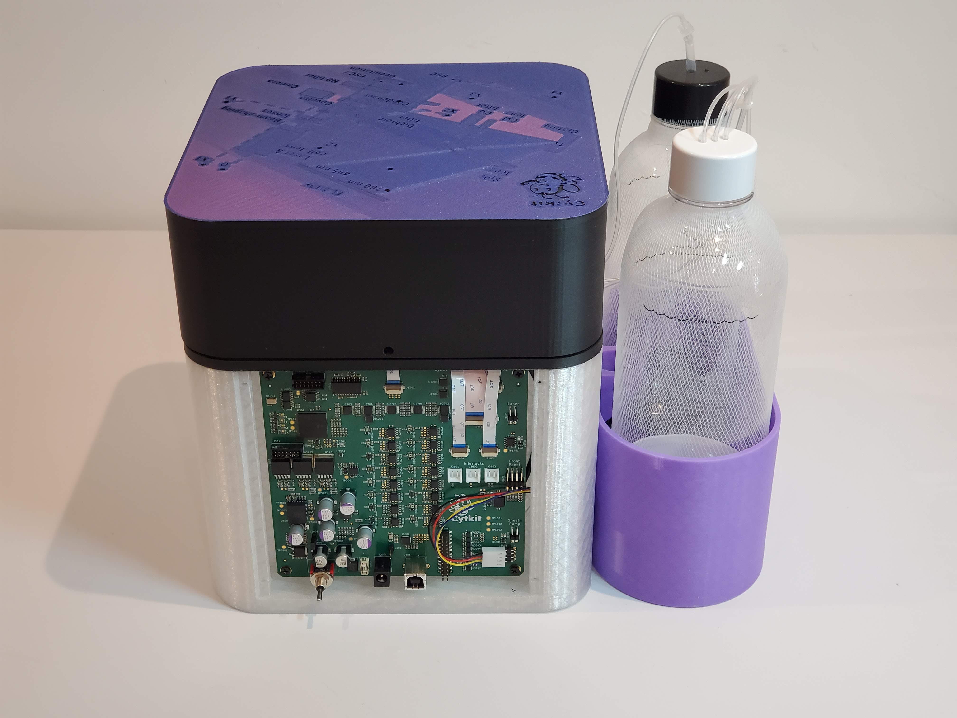
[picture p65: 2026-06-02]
build_instructions/images/build photos/20260530_181737.jpg

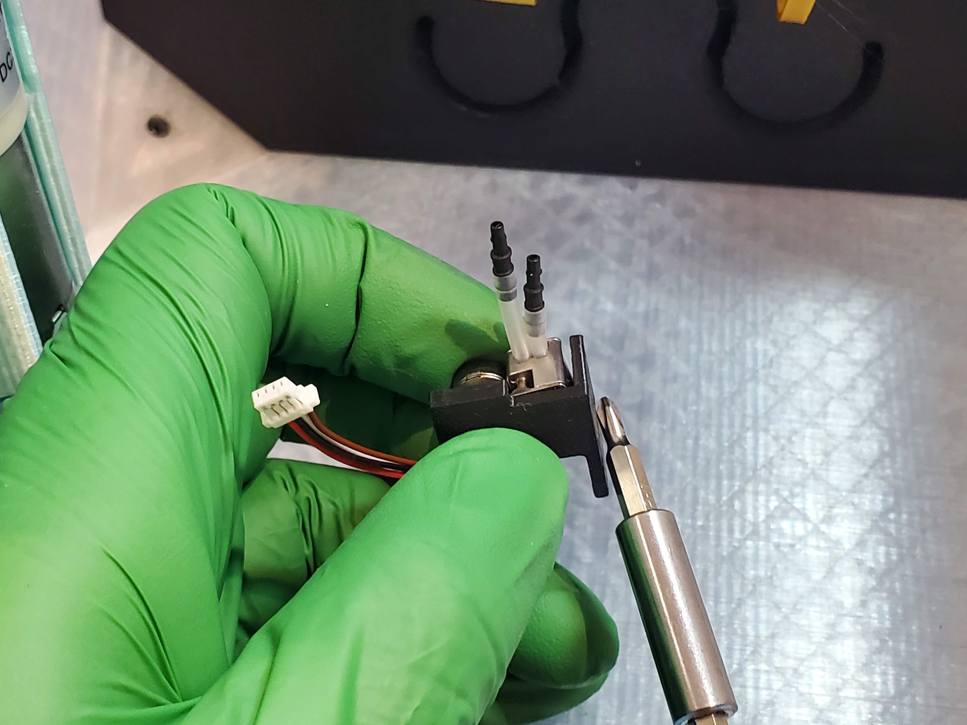
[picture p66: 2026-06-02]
build_instructions/images/build photos/20260530_130654 sample pump holder.jpg

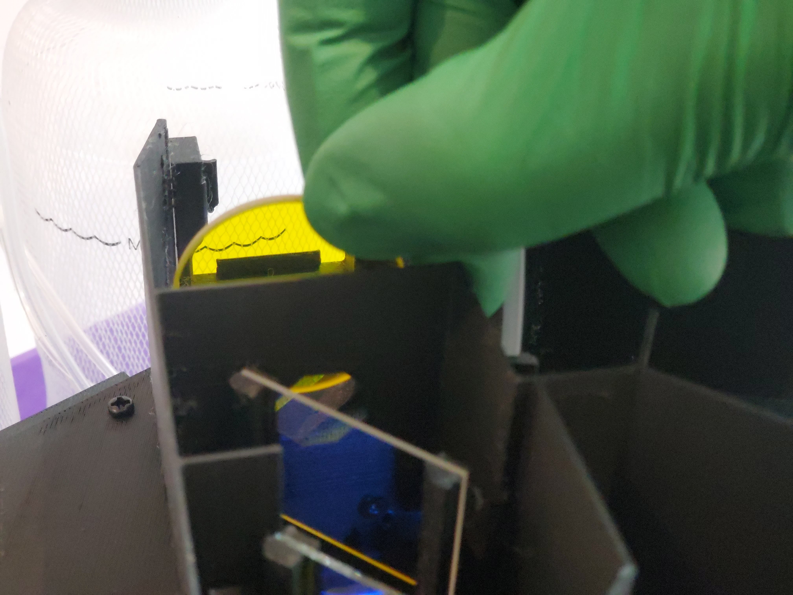
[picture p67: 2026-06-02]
build_instructions/images/build photos/20260530_145108.jpg

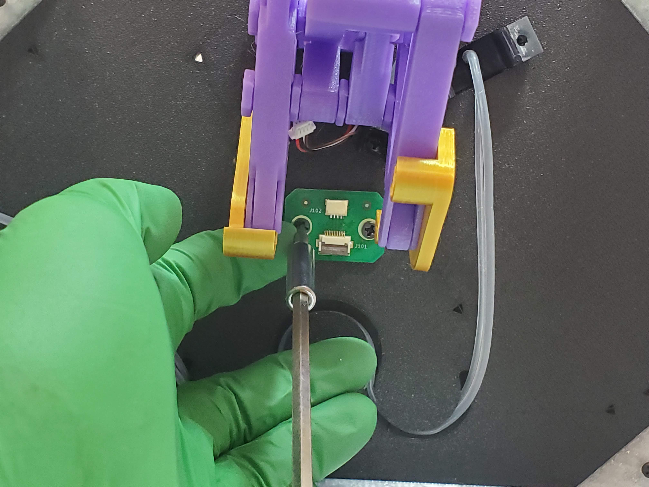
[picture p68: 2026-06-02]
build_instructions/images/build photos/20260530_132509.jpg

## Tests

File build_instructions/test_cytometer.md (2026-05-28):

# Test your Cytkit cytometer

## Clean fluidics system {pagestep}

## Flow rainbow beads {pagestep}

## Inspect data {pagestep}

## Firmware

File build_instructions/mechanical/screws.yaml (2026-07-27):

self_tapping_m3x25_hex_socket:
    Name: M3 self-tapping hex socket cap screws 25 mm (black)
    Description: Metric Screw
    Specs:
        Material: Carbon Steel (Black)
        Thread: M3
        Length: 25 mm
        Cap: internal hex cap (Allen key)
    Suppliers:
        Aliexpress:
            PartNo: 15-50pcs Black Hex Hexagon Socket Cap Head Self Tapping Screws Carbon Steel
            Link: 'https://www.aliexpress.com/item/1005004723738740.html'
self_tapping_m3x6_posi:
    Name: M3 self-tapping posi head screws 6 mm (black)
    Description: Metric Screw
    Specs:
        Material: Carbon Steel (Black)
        Thread: M3
        Length: 6 mm
        Cap: Philips/Posi
    Suppliers:
        Aliexpress:
            PartNo: Black Carbon Steel Phillips Truss Head Screw
            Link: 'https://www.aliexpress.com/item/1005009495394483.html'
self_tapping_m3x8_posi:
    Name: M3 self-tapping posi head screws 8 mm (black)
    Description: Metric Screw
    Specs:
        Material: Carbon Steel (Black)
        Thread: M3
        Length: 8 mm
        Cap: Philips/Posi
    Suppliers:
        Aliexpress:
            PartNo: Black Carbon Steel Phillips Truss Head Screw
            Link: 'https://www.aliexpress.com/item/1005009495394483.html'
self_tapping_m3x10_posi:
    Name: M3 self-tapping posi head screws 10 mm (black)
    Description: Metric Screw
    Specs:
        Material: Carbon Steel (Black)
        Thread: M3
        Length: 10 mm
        Cap: Philips/Posi
    Suppliers:
        Aliexpress:
            PartNo: Black Carbon Steel Phillips Truss Head Screw
            Link: 'https://www.aliexpress.com/item/1005009495394483.html'
self_tapping_m3x12_posi:
    Name: M3 self-tapping posi head screws 12 mm (black)
    Description: Metric Screw
    Specs:
        Material: Carbon Steel (Black)
        Thread: M3
        Length: 12 mm
        Cap: Philips/Posi
    Suppliers:
        Aliexpress:
            PartNo: Black Carbon Steel Phillips Truss Head Screw
            Link: 'https://www.aliexpress.com/item/1005009495394483.html'
self_tapping_m3x16_posi:
    Name: M3 self-tapping posi head screws 16 mm (black)
    Description: Metric Screw
    Specs:
        Material: Carbon Steel (Black)
        Thread: M3
        Length: 16 mm
        Cap: Philips/Posi
    Suppliers:
        Aliexpress:
            PartNo: Black Carbon Steel Phillips Truss Head Screw
            Link: 'https://www.aliexpress.com/item/1005009495394483.html'
m3_washers:
    Name: M3 washers
    Description: Metric washer
    Specs:
        Material: Stainless Steel
        Inner diameter: 3 mm
        Cap: Philips/Posi
    Suppliers:
        Aliexpress:
            PartNo: DIN125 Plain Washers 304 Stainless Steel
            Link: 'https://www.aliexpress.com/item/1005011840506400.html'

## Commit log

2025-05-14 updated cad to v0.32, various fixes
    [Cytkit model 0.31 12may25-Main body rev2 with test fixtures.stl, Cytkit model 0.32-Main body rev2 with test fixtures.stl]
2025-05-16 improved back panel
    [Cytkit model 0.32-Panel.stl, Cytkit model 0.32-Rear Panel.stl]
2025-05-26 minor update
    [Cytkit model 0.32-sheath chamber print flat.stl, Cytkit model 0.32-sheath chamber.stl, Cytkit model 0.32.FCStd]
2025-06-18 updated CAD, latest sheath chamber for resin printing
    [Cytkit model 0.32.FCStd, Cytkit model 0.32f-sheath chamber for resinChamfer.stl]
2026-02-27 started v0.4
    [Cytkit master assembly.FCStd, Cytkit model 0.3 10may25 sample loader assembly flat.stl, Cytkit model 0.3 10may25-Base.stl, Cytkit model 0.3 10may25-Cover.stl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]
2026-02-27 stiffer, broader sheath chamber
    [base panel cover stand cart.FCStd, main body with optics (square cuvette).FCStd, main body with optics.FCStd, sheath chamber b.FCStd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]
2026-03-06 added camera and mount
    [main body with optics.FCStd]
2026-03-06 added interlocks, improved camera lens tube
    [base panel cover stand cart.FCStd, main body with optics.FCStd, sheath pump holder.FCStd]
2026-03-14 now starting to fix snags for v0.6
    [base panel cover stand cart.FCStd, case artwork.FCStd, main body with optics.FCStd, sheath chamber.FCStd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]
2026-03-15 snag fixes
    [base panel cover stand cart.FCStd, fsc board.FCStd, main body with optics.FCStd, main pcb.FCStd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]
2026-03-28 before sample loader edit
    [base panel cover stand cart.FCStd, blower and housing.FCStd, fsc board.FCStd, main body with optics.FCStd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]
2026-04-19 coming along
    [main body with optics.FCStd]
2026-04-19 main body ready to print
    [base panel cover stand cart.FCStd, blower and housing.FCStd, fsc board.FCStd, main body with optics.FCStd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]
2026-04-21 refinements to camera mount, condensing lens mount, focusing lens mount
    [base panel cover stand cart.FCStd, main body with optics.FCStd]
2026-04-30 laser 100 mW mount
    [main body with optics.FCStd]
2026-05-01 prepared for 100mW laser, new cyl correction lens, safer adjustment of foc lenses, fl compartment cap
    [base panel cover stand cart.FCStd, main body with optics.FCStd]
2026-05-01 improvements to screens, fix to sheath chamber
    [base panel cover stand cart.FCStd, main body with optics.FCStd, sheath chamber.FCStd]
2026-05-03 improvements to stages for printing
    [base panel cover stand cart.FCStd, case artwork.FCStd, main body with optics.FCStd]
2026-05-07 improvements to laser holder, new camera mount v adjust
    [base panel cover stand cart.FCStd, main body with optics.FCStd]
2026-05-12 added pda10a, added fan holder, added cable management
    [base panel cover stand cart.FCStd, blower and housing.FCStd, main body with optics.FCStd, sheath pump holder.FCStd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]
2026-05-13 added 2nd 45deg filter
    [base panel cover stand cart.FCStd, main body with optics.FCStd]
2026-05-22 added thorlabs pd slit holder concentrator funnel
    [base panel cover stand cart.FCStd, blower and housing.FCStd, main body with optics.FCStd]
2026-05-24 added front panel logo relief
    [base panel cover stand cart.FCStd, front panel logo relief.FCStd, main body with optics.FCStd]
2026-05-25 added cover for version with thorlabs and hamamatsu detectors
    [base panel cover stand cart.FCStd, main body with optics.FCStd]
2026-05-28 added gitbuilding
    [base panel cover stand cart.FCStd, blower and housing.FCStd, case artwork.FCStd, front panel logo relief.FCStd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]
2026-05-28 documentation structure outlined
    [Holder SiPM board.stl, M10 fitting.FCStd, base panel cover stand cart-Base.stl, base panel cover stand cart-Cover.stl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]
2026-06-02 draft build instructions started
    [M10 fitting.FCStd, case artwork.FCStd, front panel logo relief.FCStd, main body with optics.FCStd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]
2026-06-05 added tube insert
    [sample loader.FCStd]
